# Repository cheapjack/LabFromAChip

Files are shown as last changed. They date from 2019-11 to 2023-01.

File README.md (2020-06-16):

# Lab-From-A-Chip

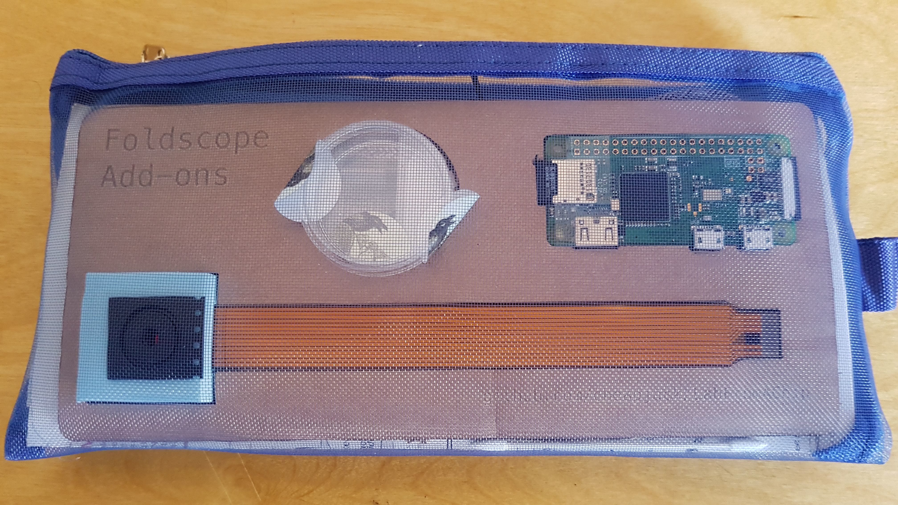
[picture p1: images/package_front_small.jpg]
Kit Component Net


Lab-from-a-chip is a DIY intervention in Lab On A Chip
technology using model organisms inspired by Science and Technology
studies and scientific practice and part of Ross Dalziel's PhD research, Critical Kits at the [Division for BioMedical Life Sciences at Lancaster University (BLS)](https://www.lancaster.ac.uk/biomedical-and-life-sciences/) and makerspace [DoESLiverpool](https://www.lancaster.ac.uk/biomedical-and-life-sciences).

*\"A* ***lab-on-a-chip*** *is a device that integrates one or several
laboratory functions on a single integrated circuit of only millimeters
to a few square centimeters to achieve automation and high-throughput
screening.\"* via
[Wikipedia](https://en.wikipedia.org/wiki/Lab-on-a-chip)

## Features

-   Hard silicon timer chips, the logical oscillating workhorses that
    make the world tick!
-   Stretchy see-through silicon polymers!
-   Lithium!
-   Model Organisms, Biology's non-human collaborators!
-   [Leeuwenhoek](https://en.wikipedia.org/wiki/Antonie_van_Leeuwenhoek)
    Microscopes made of paper with lenses ground in China on a tape reel
    just like electronic components!
-   The redundant media of Vinyl records!
-   Diodes!
-   Feminist technoscience!
-   Critters that move like animals but eat like plants!
-   Making moulds from the capitalist ruins!

## Included

 * [Foldscope](https://www.foldscope.com/) or 10x mag & up microscope
 * [PolyDiMethylSiloxane](https://en.wikipedia.org/wiki/Polydimethylsiloxane) (PDMS) Silicon
 * 2 Syringes
 * Mini Petri Dish
 * Glass or plastic Microscope slide
 * Glass coverslip
 * Instruction Booklet
 * Paperfuge Kit
 * Tweezers
 * Surplus electronics
 * 7"/12" vinyl record fragment

## Getting Started

Jump to [Getting Started](GettingStarted.md) to get going

## Background: Bridging The World-To-Chip Barrier

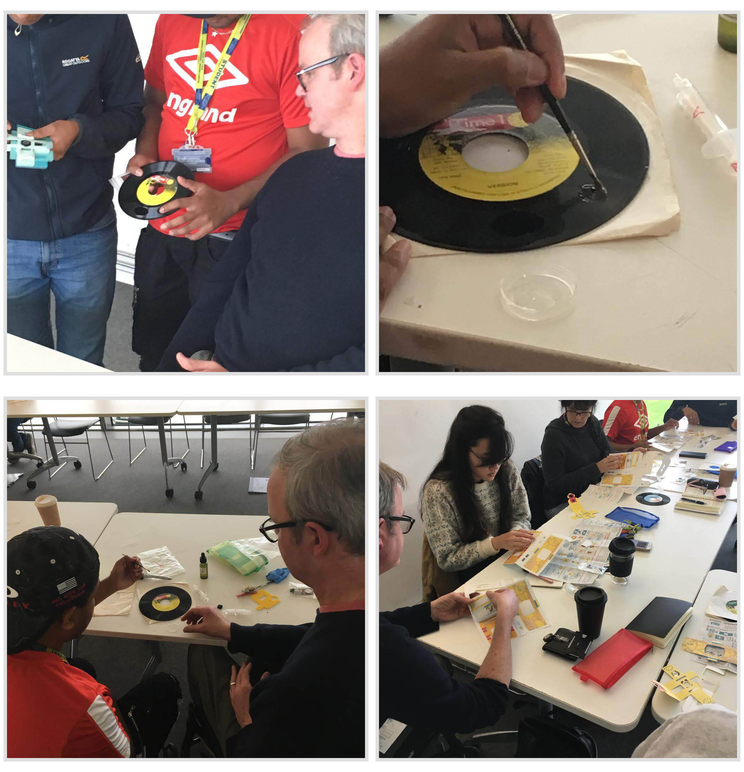
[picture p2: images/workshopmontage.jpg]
Workshop at Liverpool John Moores University with Dr Rod Dillon, 2019


This is part of Artist Ross Dalziel's art-science PhD embedded in the Division of Biomedical and Life Sciences at Lancaster University and makerspace [DoESLiverpool](https://doesliverpool.com), exploring critical making in kit cultures, *Critical Kits*. We're interested in what happens when you take a system from science and engineering, what Science and Technology Studies (STS) calls 'technoscience' and try to make it something that can be done outside of the "secluded research" (Callon et al. 2009. *Acting in an uncertain world : an essay on technical democracy* USA: MIT Press) of the science lab; how you could turn it into a DIY kit, what that entails and what that might mean.
  
We followed some diverse approaches to [DIY Microfluidics like this](http://fab.cba.mit.edu/classes/S62.12/people/tsai.liz/index.html), in our [Makerspace](https://github.com/DoESLiverpool/Wearables/wiki/Bio-Blog-2019#algae-microfluidics-doesliverpool) then began following the practices of microbiologist, researcher, biotechnologist and engineer [Alexandre Benedetto](https://www.lancaster.ac.uk/health-and-medicine/about-us/people/alexandre-benedetto).

Alex and his colleagues use the technique to observe the [organismal death process in *C elegans* model organisms](https://linkinghub.elsevier.com/retrieve/pii/S2211124718302316).Alex and his colleagues developed a method using the grooves of old vinyl records as moulds for PDMS silicon which centrifuged and de-gassed, provides optically clear environments for securing nematodes for the observation of gene expression and other processes.
 
We take ideas from STS and feminist technoscience to make a [Theoretical Repertoire](TheoreticalRepertoire.md) and develop a kit and workshop exploring model organisms in DIY environments made from discarded domestic electronics and media.

*"Microfluidic devices are an enabling technology for many labs,
facilitating a wide range of applications spanning high-throughput
encapsulation, molecular separations, and long-term cell culture. In
many cases, however, their utility is limited by a 'world-to-chip'
barrier that makes it difficult to serially interface samples with these
devices."*

(Longwell, Scott A, and Fordyce, Polly M. 2019. *micrIO: an open-source
autosampler and fraction collector for automated microfluidic
input--output* London Royal Society of Chemistry)

This world and it's related fields of engineering of pico, nano and microfluidics can be hard to get into. Engineering structures only a few tens of microns high are hard and expensive to make. Our project tries to take a playful approach to fostering agency and embodied thinking about this technology and bringing silicon and big living collaborating proteins (us humans) together.
 
We realised we are already surrounded by exotic objects that are made of very small engineered structures: the tiny logos etched onto integrated circuits in our phones or humble doorbell, or the tiny grooves of a vinyl record. All you need is some Polydimethylsiloxane (PDMS) a *silicon polymer* that is inert, non-toxic and optically clear to use these exotic objects to manipulate living organisms. What these chips really depend on is microfluidics, a development from electronic circuits but with things much bigger than electrons, the big molecules of chemistry and biology.
  
*"Microfluidic devices are powerful tools for biology, chemistry, and
medicine, with applications including biomolecular characterization,
cell encapsulation and culture, particle synthesis, and diagnostics. In
theory, their miniature scale allows a researcher to integrate processes
that span several lab benches into a single device with minimal cost and
sample requirements. In reality, the extensive infrastructure required
to convey reagents, samples, and analytes into and out of devices often
renders a 'lab-on-a-chip' more of a 'chip-in-a-lab"* (Ibid.)

Making this technology involves dust free environments, vacuum systems and expensive photolithography to get it done 'right'. But this usually does not stop the DIY 'maker' impulse. Even [Scanning Tunneling Microscopes (STM)](http://dberard.com/home-buit-stm) have gone DIY.  There is alot of open source work going on in the microfluidic community, not necessarily DIY, but I'm exploring how makerspaces can engage with it.

In experimenting with DIY microfluidics I hope to

-   Teach what microfluidics really are away from the master hyperbolic
    sales talk of Lab on A Chip.
-   Explore 'agency' and the power relations and subjectivities so other
    actors can explore the field
-   See what is going on in the technology

Make a *"frame for recovering the heterogeneous relations that technologies fold together...to be...re-enacted differently"* (Lucy Suchman, In Lury, C. and Wakeford, N. eds. (2012) Inventive methods: The happening of the social. London: Routledge. pp. 62-74.)

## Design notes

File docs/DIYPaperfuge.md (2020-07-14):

# DIY Paperfuge

Another Prakash Lab project, the makers of your Foldscope, is the Paperfuge, an "ultra-low cost, light-weight, field-portable centrifuge" based on the physics of a whirligig childrens toy. Our DIY version won't reach speeds of their design; but like our mould making, is 'just-good-enough' to let us follow a craft techniques in science. 

Recently some of their community used a [Dynamo torch](https://www.ebay.co.uk/itm/Pack-Hand-Pressing-3LED-Crank-Power-Dynamo-Wind-Up-Flashlight-Torch-Light-New/263717065208) using the mechanism to make the [Handyfuge](https://github.com/ethanjli/handyfuge). We're looking into remixing Bioengineer Ethan's design to fit our mini petri dishes as we'd get much faster spinning speeds. 

A centrifuge is a key tool in seperating the different parts of a solution like blood, cultured organisms or pond water. It's also a key part of preparing biological assays for [PCR](https://en.wikipedia.org/wiki/Polymerase_chain_reaction) or [LAMP](https://en.wikipedia.org/wiki/Loop-mediated_isothermal_amplification) diagnoses. 

Once you've mixed your PDMS carefully secure the lid (it's the bigger part) with the sellotape included, cut out the paperfuge design & push into the middle of the cut folds in your 'fuge & tape securely in position.

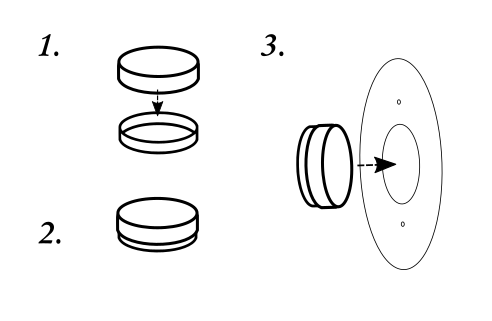
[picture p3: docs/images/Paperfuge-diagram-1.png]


## Cut out and make your Paperfuge 

Once you've mixed your PDMS, and before impressing our chip or vinyl fragment we will try to use the spin of the motion of a whirligig, the paperfuge. as a centrifugal force to 'push' the mix to the sides to make it nice & thin & even. 

Ideally we would assemble all our components in a dust & microbe free environment so we only see in the microscope what we might expect to see. For us, strange artefacts or particles from the unique histories of our moulds are encouraged!  

_Read the original Paperfuge research paper [here](http://dx.doi.org/10.1101/072207)_

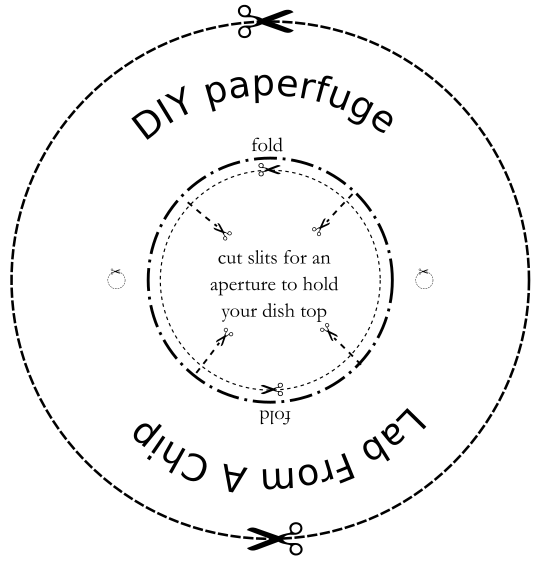
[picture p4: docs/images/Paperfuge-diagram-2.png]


Now thread the twine through the holes as below & tie off with a knot

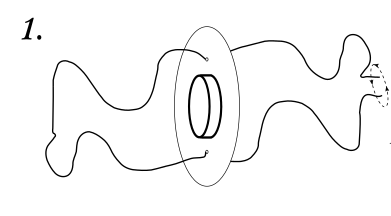
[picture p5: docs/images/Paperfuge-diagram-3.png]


Hold each end in front of you & start letting the disc rotate in front of you so that the twine starts to twist into a helix, it takes quite some time keep going! 
 
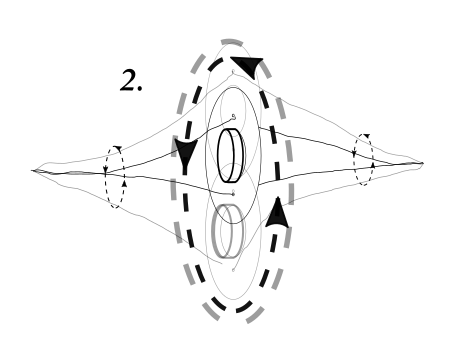
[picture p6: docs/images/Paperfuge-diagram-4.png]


Once twisted quickly pull the bunched up helix outwards to the side & watch it spin! The bigger the twist the faster your spin! Try it a few times before you make your vinyl or chip impression and set

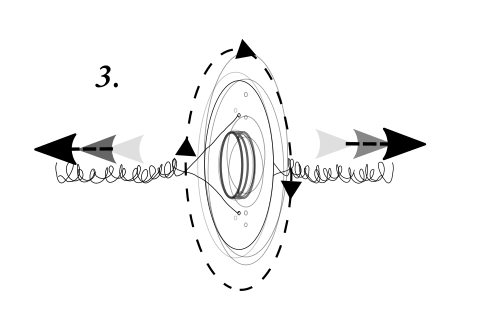
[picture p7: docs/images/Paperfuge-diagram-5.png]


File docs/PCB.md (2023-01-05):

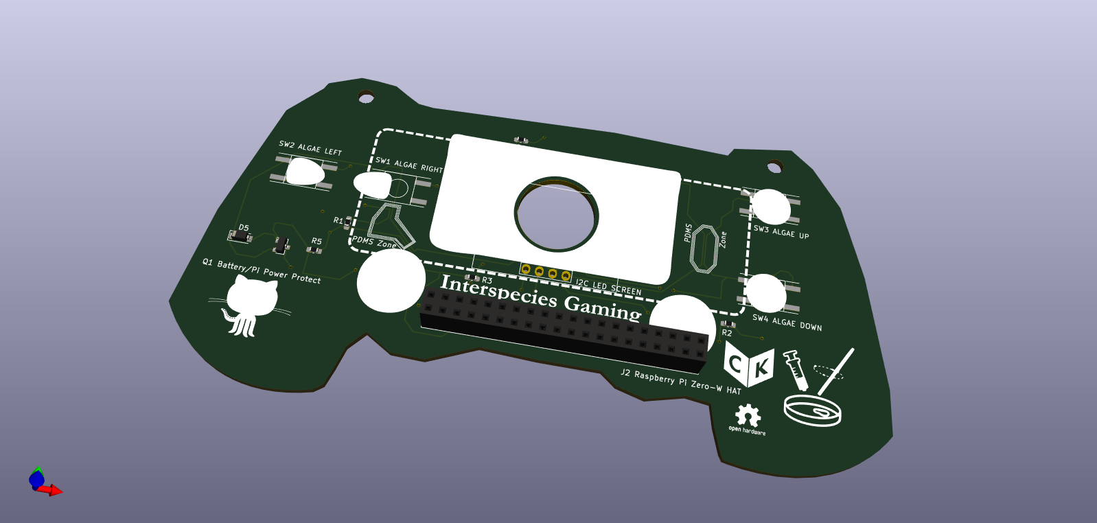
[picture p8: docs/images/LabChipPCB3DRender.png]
KiCAD render of the Lab From A Chip PCB Handheld Biotic Game Controller


## Lab From A Chip PCB 💾🔬🧪

The Lab From A Chip Printed Circuit Board (PCB) is a prototype game platform and Critical kit made using *Interleaving Practices*, a methodology developed by artist Ross Dalziel in his PhD research project at LICA (Lancaster Institute for Contemporary Arts) and the Division for BioMedical Life Sciences at Lancaster University (BLS) and makerspace DoESLiverpool. It is an 'add-on' kit for the *Foldscope*, a folding paper microscope by Prakash Labs.

Like the main Lab From A Chip project it's a material critique of bio-technology by way of an intervention in the field of what makers and researcher's like Riedel-Kruse et al. (2011) call 'biotic gaming' and Lamers and van Eck described in their review of key examples, 'Why Simulate? Hybrid Biological Digital Games' (2012), where 'live organisms are an integral part of digital gaming technology or player experience'. It followed from preliminary discussions of the idea of *Interspecies Gaming* with artist Isabel Paehr at the Disrupt Encode Consilidate international symposium organised by Dalziel and his colleagues and supervisors Neil Dawson and Rod Dillon at BLS in 2018. 

The PCB is not a novel art-science-tech object but rather the by-product of learning through careful critical making exploring how maker culture and microbiologists both exploit and care for each other through technology, in the case of makers and the non-human, in the case of biologists.

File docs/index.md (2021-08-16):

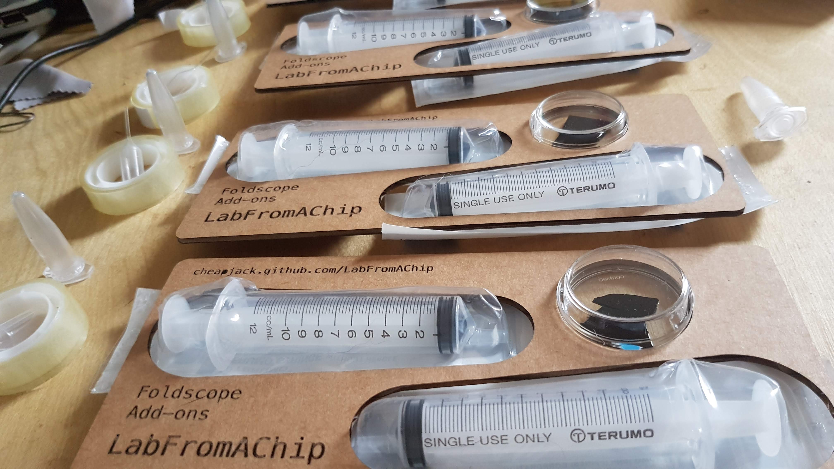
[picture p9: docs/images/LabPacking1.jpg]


Lab-from-a-chip is a DIY intervention in Lab On A Chip technology using model organisms inspired by Science and Technology studies and scientific practice and part of Ross Dalziel's PhD research, Critical Kits at the [Division for BioMedical Life Sciences at Lancaster University (BLS)](https://www.lancaster.ac.uk/biomedical-and-life-sciences/) and makerspace [DoESLiverpool](https://www.lancaster.ac.uk/biomedical-and-life-sciences).

*\"A* ***lab-on-a-chip*** *is a device that integrates one or several laboratory functions on a single integrated circuit of only millimeters to a few square centimeters to achieve automation and high-throughput screening.\"* via
[Wikipedia](https://en.wikipedia.org/wiki/Lab-on-a-chip)

We include a standard Foldscope kit fresh from the [Foldscope Shop](https://www.foldscope.com/) and have included some extra materials to help you get started in the world of DIY microfluidics. We include a sample test glass microscope slide ready to use with your foldscope which can be assembled from the pop out net of coloured paper components.

## Getting Started

Go to [Getting Started](./GettingStarted.md) to get making!

## Features

-   Hard silicon timer chips, the logical oscillating workhorses that
    make the world tick!
-   Stretchy see-through silicon polymers!
-   Model Organisms, Biology's non-human collaborators!
-   [Leeuwenhoek](https://en.wikipedia.org/wiki/Antonie_van_Leeuwenhoek) Microscopes made of paper with lenses ground in China on a tape reel just like electronic components!
-   The redundant media of Vinyl records!
-   Critters that move like animals but eat like plants!
-   Making moulds in the capitalist ruins!

## Included

Item|Number|Source
---|---|---
Foldscope|1|[Foldscope Shop](https://www.foldscope.com/)
[PolyDiMethylSiloxane](https://en.wikipedia.org/wiki/Polydimethylsiloxane)(PDMS) Silicon|1|[EBay Shop](https://www.ebay.co.uk/itm/0-5kg-Clear-Electronic-Potting-Compound-PV-Solar-Cell-Encapsulant-PDMS-RV/323393673289)
2 pouches with syringes `A` & `B`|2|[EBay Shop](https://www.ebay.co.uk/itm/Terumo-Sterile-Syringes-Hypodermic-Luer-Slip-Syringe-1ml-2-5ml-5ml-10ml-20ml-30m/263962579871)
35mm Mini Petri Dish|1|[EBay Shop](https://www.ebay.co.uk/itm/10-Pcs-Laboratory-Plastic-Petri-Dish-Sterile-Cell-Tissue-Culture-Dishes-35mm/292809086404)
Glass Microscope slide|1|[EBay Shop](https://www.ebay.co.uk/itm/Professional-50-pcs-Blank-Microscope-Slides-Cover-Glass-Lab-Prep-ground-edges/283412415605)
Pre-prepared glass microscope slide|1|DoESLiverpool community
Instruction Booklet|1|cheapjack
Tweezers|1|[EBay](https://www.ebay.co.uk/itm/10PC-TWEEZER-SET-FOR-PRECISE-ELECTRONICS-MODELLING-JEWELLERY-BEADING-WIRE-WORK/173541962441)
Surplus electronic chip|1|[EBay](https://www.ebay.co.uk/itm/NE555-Timer-Chips-5-Pack-IC-PCB-Free-UK-P-P/231668892136)
7"/12" vinyl record fragment|1|Found in a flat in the Holly Street Estate, Hackney 1996

<!--Glass coverslips|3|[Ebay Shop](https://www.ebay.co.uk/itm/100-Glass-Micro-Cover-Slips-Glass-Blank-Lab-Coverslip-Microscope-Slide-Cover/164281210287)-->

## Bridging The World-To-Chip Barrier

Workshop at Liverpool John Moores University with Dr Rod Dillon, 2019

This is part of Artist Ross Dalziel's art-science PhD embedded in the Division of Biomedical and Life Sciences at Lancaster University and makerspace [DoESLiverpool](https://doesliverpool.com), exploring critical making in kit cultures, *Critical Kits*. We're interested in what happens when you take a system from science and engineering, what Science and Technology Studies (STS) calls 'technoscience' and try to make it something that can be done outside of the "secluded research" (Callon et al. 2009. *Acting in an uncertain world : an essay on technical democracy* USA: MIT Press) of the science lab; how you could turn it into a DIY kit, what that entails and what that might mean.

We followed some diverse approaches to [DIY Microfluidics like this](http://fab.cba.mit.edu/classes/S62.12/people/tsai.liz/index.html), in our [Makerspace](https://github.com/DoESLiverpool/Wearables/wiki/Bio-Blog-2019#algae-microfluidics-doesliverpool) then began following the practices of microbiologist, researcher, biotechnologist and engineer [Alexandre Benedetto](https://www.lancaster.ac.uk/health-and-medicine/about-us/people/alexandre-benedetto).

Alex and his colleagues use the technique to observe the [organismal death process in *C elegans* model organisms](https://linkinghub.elsevier.com/retrieve/pii/S2211124718302316). Alex and his colleagues developed a mehtod using the grooves of old vinyl records as moulds for PDMS silicon which centrifuged and de-gassed, provides optically clear environments for securing nematodes for the observation of gene expression and other processes.

We take ideas from STS and feminist technoscience to make a [Theoretical Repertoire](./TheoreticalRepertoire.md) and develop a kit and workshop exploring model organisms in DIY environments made from discarded domestic electronics and media.

*"Microfluidic devices are an enabling technology for many labs,
facilitating a wide range of applications spanning high-throughput
encapsulation, molecular separations, and long-term cell culture. In
many cases, however, their utility is limited by a 'world-to-chip'
barrier that makes it difficult to serially interface samples with these
devices."*

(Longwell, Scott A, and Fordyce, Polly M. 2019. *micrIO: an open-source
autosampler and fraction collector for automated microfluidic
input--output* London Royal Society of Chemistry)

This world and it's related fields of engineering of pico, nano and microfluidics can be hard to get into. Engineering structures only a few tens of microns high are hard and expensive to make. Our project tries to take a playful approach to fostering agency and embodied thinking about this technology and bringing silicon and big living collaborating proteins (us humans) together.

We realised we are already surrounded by exotic objects that are made of very small engineered structures: the tiny logos etched onto integrated circuits in our phones or humble doorbell, or the tiny grooves of a vinyl record. All you need is some Polydimethylsiloxane (PDMS) a *silicon polymer* that is inert, non-toxic and optically clear to use these exotic objects to manipulate living organisms. What these chips really depend on is microfluidics, a development from electronic circuits but with things much bigger than electrons, the big molecules of chemistry and biology.

*"Microfluidic devices are powerful tools for biology, chemistry, and
medicine, with applications including biomolecular characterization,
cell encapsulation and culture, particle synthesis, and diagnostics. In
theory, their miniature scale allows a researcher to integrate processes
that span several lab benches into a single device with minimal cost and
sample requirements. In reality, the extensive infrastructure required
to convey reagents, samples, and analytes into and out of devices often
renders a 'lab-on-a-chip' more of a 'chip-in-a-lab"* (Ibid.)

Making this technology involves dust free environments, vacuum systems and expensive photolithography to get it done 'right'. But this usually does not stop the DIY 'maker' impulse. Even [Scanning Tunneling Microscopes (STM)](http://dberard.com/home-buit-stm) have gone DIY.  There is alot of open source work going on in the microfluidic community, not necessarily DIY, but I'm exploring how makerspaces can engage with it.

In experimenting with DIY microfluidics I hope to

-   Teach what microfluidics really are away from the master hyperbolic
    sales talk of Lab on A Chip.
-   Explore 'agency' and the power relations and subjectivities so other
    actors can explore the field
-   See what is going on in the technology

Make a *"frame for recovering the heterogeneous relations that technologies fold together...to be...re-enacted differently"* (Lucy Suchman, In Lury, C. and Wakeford, N. eds. (2012) Inventive methods: The happening of the social. London: Routledge. pp. 62-74.)

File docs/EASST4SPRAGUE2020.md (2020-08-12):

#  Lab From A Chip
Programme of Making and Doing Session at [EASST4SPRAGUE2020](https://www.easst4s2020prague.org/)

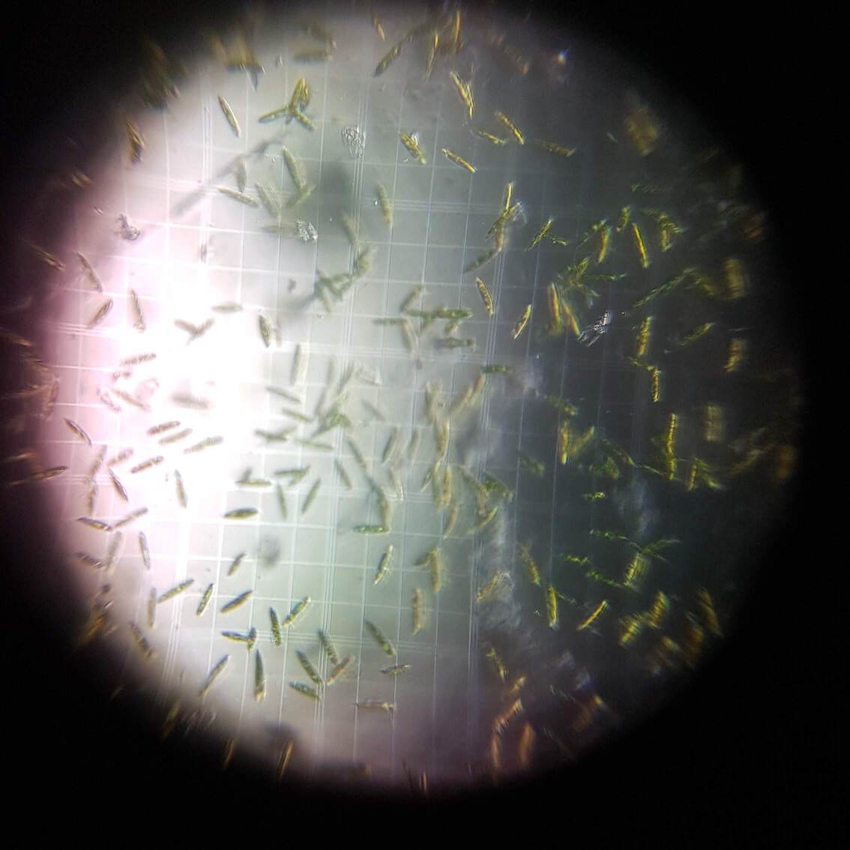
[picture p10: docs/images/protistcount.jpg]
*Euglena gracilis* on a hemocytometer viewed under a DIY lasercut microscope


## Getting Started

Already received your kit? Head over to the [Getting Started Guide](GettingStarted.md)

## Abstract

We ask questions as we build little logical maps together with *Euglena gracilis*; why are diodes so cheap, how do worms die? What organisms should we play with and how do old 7-inch vinyl records, Printed Circuit Boards (PCB's), Integrated circuits (IC's) A.K.A. silicon chips and other surplus domestic artefacts provide physical spaces to tell stories and learn critical knowledge? We explore this through 'kit culture', hands-on by using a prototype 'educational' kit and the emerging method of 'Interleaving Practices', part of artist-researcher Ross Dalziel's art-science practice and PhD research embedded in Lancaster University.

## Brief Description

Remote hands on making & doing session, featuring paper folding microscopy and micro-fluidics, so called 'lab-on-a-chip' technology. Materials will be provided as a kit posted to `EASST4SPRAGUE2020` participants who sign up to the activity prior to the online conference. Participants in their homes or safe spaces, will be led remotely by the artist-presenter-researcher on a screen sharing video platform in a making and doing session with these kits at `EASST4SPRAGUE2020`.

 Our new worlds of locating and timing is an opportunity to warp the time of the activity we normally get to engage with each other at our EASST meetings; the 'educational kit' format the session uses allows us to do this; some of the activity needs 1 or 2 days preparation and experiment prior to the activity, so the session will require some commitment to playing with materials to get the most out of it.

 We'd like to focus on all of our experiences with the kit so we see this as an experimental and informal show and tell more than a presentation online. Numbers are limited to available kits so we have a core group of engaged people.

We'll provide more information to participants who sign up with respect to online presentation dates and timings soon. We'll also include further information on the PhD research behind the session with an opportunity to engage further and health and safety information with respect to the packing and preparation of the kits.

We also welcome ongoing engagement and hope we can start some kind of collective and engage further with all of our research practices.

The project homepage provides updated further information and guidance

[cheapjack.github.io/LabFromAChip/](https://cheapjack.github.io/LabFromAChip/)

## Methods

It's a playful DIY approach to kit making, a key feature of Ross' work and his collaborators at [Domestic Science](https://domesticscience.org.uk/) and [DoESLiverpool](https://doesliverpool.com/). These kits are emerging, messy and unfinished; they 'bag up' & include existing kits, primarily the [Foldscope](https://www.foldscope.com/) and are at once a kind of literature review, fan-non-fiction and remix; your interactions will inform their future story. Once you receive your kit you will be able to use model organisms and surplus integrated circuits (IC's) included, the black boxes of microbiology and computer science. We'll learn how to make DIY micro-fluidic moulds, following the practices observed in Ross' research developed by researchers and teaching staff in the Division of Biomedical and Life Sciences (BLS) at Lancaster University.

For us science studies is a theoretical repertoire for a form of 'critical making', implosions & configuration methods (Ratto, Haraway, Dumit, Suchman) developed in an art practice embedded in microbiological pedagogy, the teaching space of BLS Lancaster and makerspace culture. The repertoire helps us 'unbox' an "infinity of traces" where the convenient mobilities of PCBs, biotech and interspecies gaming become not-so-humble-bundles of love, education, mobility, identity and inequality.

This helps inform, 'Interleaving practices' the artist-researchers emerging method for working with people in the diverse disciplines and domains of biomedical technoscience using the format of what we think of as 'kit culture', a mix of so-called STEAM education and makerspace culture. From here we negotiate the "World to chip barrier" (Longwell, Scott A, and Fordyce, Polly M. 2019. *micrIO: an open-source autosampler and fraction collector for automated microfluidic input–output London Royal Society of Chemistry*) where the 'revolutionary' promise of 'Lab-On-A-Chip' technology often becomes "A-Chip-In-A-Lab" (Ibid.). Kits here are boundary objects to support ongoing, troubling and messy explorations of biopolitics and cross species value extraction and a chance to see how much of this can be carried along in a kit format.

Participants having received their kits will use included [Foldscopes](https://www.foldscope.com/) with their smartphones and other included DIY lab materials to make non-toxic Polydimethylsiloxane (PDMS) silicon moulds from surplus 555 timer chips and the grooves of a fragment of a 7 inch vinyl record from a long gone Lovers Rock record label. Together, online and in our hands, we will try to play with, yet fail to care-for-fully, Euglena gracilis a heterotrophic protist algae, as hungry and motile as an animal, yet as resilient as a photosynthesising plant.

## Relevance

The silicon chip is a substrate for knowledge and mobility, enabling both washing machines and big DNA data, Gutenberg style embodiments of knowledge and punitive discipline, shaped by specific historical material arrangements. Data colonialism, public imaginaries and commons work upon it and through it. The who, how, why and where of making and maintaining them, matters. They are a political cut in the world, a revolutionary space, yet the masters tools for the master's house. We follow the hyperbole and reality of Lab On A Chip bio-tech to try to develop hybrid forums to re-configure these devices, the geographies they make and the crises they work in.

Ultimately we explore how much of this can be carried along in a cheap easy to distribute kit of materials and what ways of knowing it can be part of.

## Thematic Clusters

Experiments in Collaboration and Critical Participation
Multispecies Assemblages, Life Sciences, Queer Ecologies

## Other Thematic Cluster

Material activism, Kit making culture

## Technical Information

Online video platform information will be provided.
[Included](https://cheapjack.github.io/LabFromAChip/#included)

## Project URL

[cheapjack.github.com/LabFromAChip](https://cheapjack.github.com/LabFromAChip)

## Author
(Presenter-Artist-Researcher)
<a href="mailto:r.dalziel@lancaster.ac.uk?subject=Lab From A Chip at EASST4SPRAGUE2020">Ross Dalziel</a> 

## Getting Started

Already have your kit? checkout the [Getting Started guide](https://cheapjack.github.io/LabFromAChip/GettingStarted)

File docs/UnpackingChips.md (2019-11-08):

## Wednesday 13th November 2019

### STS Work in Progress



## What STS methods am I actually using?

Case Study
Configurations?
ethnography,
actor network theory,
Social practice theory,
art interventions,
digital methods

## Theoretical Repertoires

The impact of my literature review is the enriching of theoretical repertoires, which means all of the above can be unpacked. I pay attention differently now.

## What is unpacked from my PDMS chip impression?

* Just using mass produced waste or an existing manufactured item like this rather than building a fresh expensive photo-lithographic microfluidic plate, using 'cheap' domestic sources, similar to Alex's students using vinyl records, means discussions can be had about everything from supply chains, to the 'social' cost of mass manufacturing and it's histories of imperialist labor extraction
* This coincides with the of tracking supply chains and energy toxicity; Adrian and I have suggested adding fields to the BOM `.tsv` files to include where it was made, by whom and some sort of energy/carbon useage.
* So for my wearable sensor badge we'll be calculating and including this information as part of the tutorial and documentation of the kit. We want to normalise the practice of including bodily material histories.
* **Coomassie Blues**: an idea Rod & I had about exposing the supply chains and histories of the day to day materials used in microbiology lab practices
* ***Staying with the trouble*** by using things `already-dug-out-of-the-ground`
* Callback: The Biol387 students use Wilkos as their source for studying the genetic geneaology of yeast
* They help me when I need to explain critical kits to science students and scientists
* Using an ESP32 integrated circuit attracts makers interested in IoT; it's the arduino of IoT. It can start conversations about scale & micromilling in electronics production; and then alongside:
   * Why the algae? why the annoying externalities excluded from manufacturing?
   * A good chip needs to be isolated from the world and you need to make a million of them before young people can access them... etc
   * How do we protect rivers from the market imperative to make LEDs for £0.001?
     * Adrian McEwen and
* It's part of a series of FoldScope 'add-ons' that I've been making inspired by Lucy Suchman's *'artful integrations'*
  * Pi Zero Camera Twitch streaming Add-on based on [Makespace Live](https://github.com/DynamicDevices/makespacelive)
  * A wearable add on to help steady foldscopes in the field for wheelchair users
  * Microfluidic stickers to capture microfluidic environments
* Deciding to place my work in the 'domestic' or on a golf course, or in a makerspace; **i.e.** definitively in the social and not some independent ontology of art is a specific decision. It's a political 'cut'. My enriched repertoire has made me see what cuts I am making.    

### Lab-from-a-chip

Unboxing the PDMS Death Disco: A Case Study of FoldScope by making add-on Kits

[Critical Kit PDMS tweet with video of algae](https://twitter.com/CriticalKits/status/1171435079953833985)

I have been making microfluidic environments by making impressions of discarded electronics in the makerspace, based on Alex Benedetto and I talking about doing this in domestic environments; like kitchen cloths electronics, utensils or textiles.

This is partly a review of the FoldScope which Im using as a case study in my literature review.

It has all the intersections of biology, engineering, well meaning utility and agency for frugal science in 'intractable' places

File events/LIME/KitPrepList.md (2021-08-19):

## Kit Prep

## Shopping List

Item|Number|Source|In Stock|Ordered|Notes|Cost
---|---|---|---|---|---|---
Foldscope|1|[Foldscope Shop](https://www.foldscope.com/)|<input type="checkbox" checked>|<input type="checkbox" unchecked>||£0
Disposable hand pipette|20|[EBay](#)|<input type="checkbox" unchecked>|<input type="checkbox" unchecked>||£3
1.5ml Eppendorf Tube with click lid|20|[EBay](#)|<input type="checkbox" unchecked>|<input type="checkbox" unchecked>||£3
[PolyDiMethylSiloxane](https://en.wikipedia.org/wiki/Polydimethylsiloxane)(PDMS) Silicon|1|[EBay Shop](https://www.ebay.co.uk/itm/0-5kg-Clear-Electronic-Potting-Compound-PV-Solar-Cell-Encapsulant-PDMS-RV/323393673289)|<input type="checkbox" checked>|<input type="checkbox" unchecked>||£18.50
2 pouches with syringes `A` & `B`|20|[EBay Shop](https://www.ebay.co.uk/itm/Terumo-Sterile-Syringes-Hypodermic-Luer-Slip-Syringe-1ml-2-5ml-5ml-10ml-20ml-30m/263962579871)|<input type="checkbox" unchecked>|<input type="checkbox" unchecked>||£7.99
Sticker Set|20|Sticker Company|<input type="checkbox" unchecked>|<input type="checkbox" unchecked>||£10
35mm Mini Petri Dish|20|[EBay Shop](https://www.ebay.co.uk/itm/223684097317)|<input type="checkbox" unchecked>|<input type="checkbox" unchecked>||£5.62
Glass Microscope slide|20|[EBay Shop](https://www.ebay.co.uk/itm/203458550468)|<input type="checkbox" unchecked>|<input type="checkbox" unchecked>||£4.50
Pre-prepared glass microscope slide|20|DoESLiverpool community|<input type="checkbox" checked>|<input type="checkbox" unchecked>||£0
Instruction Booklet|20|cheapjack|<input type="checkbox" unchecked>|<input type="checkbox" unchecked>||£35
Tweezers|1|[EBay](https://www.ebay.co.uk/itm/10PC-TWEEZER-SET-FOR-PRECISE-ELECTRONICS-MODELLING-JEWELLERY-BEADING-WIRE-WORK/173541962441)|<input type="checkbox" unchecked>|<input type="checkbox" unchecked>||£13.77
Surplus electronic chip|20|[EBay](https://www.ebay.co.uk/itm/NE555-Timer-Chips-5-Pack-IC-PCB-Free-UK-P-P/231668892136)|<input type="checkbox" unchecked>|<input type="checkbox" unchecked>||£12.30
7"/12" vinyl record fragment|20|Found in a flat in the Holly Street Estate, Hackney 1996|<input type="checkbox" checked>|<input type="checkbox" unchecked>||£0
*LIME TOTAL*||||||**£54.18**

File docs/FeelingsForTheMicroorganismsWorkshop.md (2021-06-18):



Lab-from-a-chip is a kit for collaborating with microscopic model organisms - freshwater algae - inspired by the practices of microbiology, maker culture and Science and Technology studies, part of artist Ross Dalziel's PhD research - a form of art-science - at the [Division for BioMedical Life Sciences at Lancaster University (BLS)](https://www.lancaster.ac.uk/biomedical-and-life-sciences/) and makerspace [DoESLiverpool](https://www.lancaster.ac.uk/biomedical-and-life-sciences).

With collaborators at [Domestic Science](https://domesticscience.org.uk/) our workshop uses safe simple accessible micro moulding techniques to interact with the microscopic material surfaces of our everyday modern world - the surfaces of a microchip, an old vinyl record, the texture of a phone case - with living photosynthetic algae.  

We use a standard Foldscope kit fresh from engineer Manu Prakash's [Foldscope Shop](https://www.foldscope.com/) with extra materials to help people explore the world of DIY microfluidics.

## Feeling For the Microorganims

We are inspired by Evelyn Fox Keller's fascinating biography of geneticist Barbara McClintock, *A Feeling For The Organism* and the intimate care for living things - human and non-human - required of all workers in the life sciences. This workshop aims to explore and reflect on the value of everyday biomedical research and practice - a 21st century domestic science that considers everyone's labour - particularly in biomedicine, health and wellbeing - and aims to reconnect to our passions to look after organisms other than ourselves. 

## Features

 * Play with silicon chips and the surfaces of the technoscientific materials we use everyday.  
 * Pay with stretchy see-through hands on food safe silicon polymers!
 * Model Organisms, Biology's non-human collaborators!
 * [Leeuwenhoek](https://en.wikipedia.org/wiki/Antonie_van_Leeuwenhoek) style DIY orgigami Microscopes by [Foldscope](https://www.foldscope.com/)
 * *Euglena gracilis* algae, critters that move like animals but eat like plants
 * Making microscopic moulds from everyday technology and capturing images with smartphones, computers and the naked eye

## Background

Workshop at Liverpool John Moores University with Dr Rod Dillon, 2019

This is part of Artist Ross Dalziel's art-science PhD embedded in the Division of Biomedical and Life Sciences at Lancaster University and makerspace [DoESLiverpool](https://doesliverpool.com), exploring critical making in kit cultures, *Critical Kits*. We're interested in what happens when you take a system from science and engineering, what Science and Technology Studies (STS) calls 'technoscience' and try to make it something that can be done outside of the "secluded research" (Callon et al. 2009. *Acting in an uncertain world : an essay on technical democracy* USA: MIT Press) of the science lab; how you could use this to reflect on healthy relationships, care and maintenance of the world .

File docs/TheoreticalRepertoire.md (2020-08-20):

## Theoretical Repertoire 📚 📦

See [our theory presentation here](https://fuzzy-scabiosa.glitch.me/)

In my research on kit culture, I try to build up a theoretical
repertoire for tuning into what might be going on across various forms
of biological knowledge production, then use this repertoire to make
kits, a kind of `critical-making`.

These kits then become handy "boundary objects", objects that people
from different disciplines or practices can use or understand, for
exploring further and more intimately, growing the repertoire, making
more kits with more people and so on. In my case they allow an artist
doing research, 'laypersons'(different 'publics') and
'specialists'(scientists and their students) understand each other.

But also and this is what I now understand as a big part of my artistic
practice and the practice of [Domestic
Science](https://domesticscience.org.uk/about.html), most commonly the
kits and activities I make and facilitate become objects to talk over
and around.

I build the repertoire by reading through making, making through reading
and talking.

-   Review a range of kit and kit like practices that condense into a
    [Library of
    kits](https://domesticscience.org.uk/criticalkits/Library.html), a
    kit literature.
-   Briefly review literatures of the history of the philosophy of
    science in response to practices and kits I make with people.
-   Review literatures in STS Method, structured by emerging kits.

With this repertoire and armed with my boundary negotiating kits:

-   Observe Craft practices in teaching microbiology undergraduates at
    the Division for Biomedical Life Science at Lancaster University
-   Observe me making kits with researchers and students
-   Making kits and facilitating activity based on them in makerspace
    DoESLiverpool and other sites in the worlds related to my art
    practice.

### Imaginaries

STS method includes the use of ethnographic or other styles of 'case
study'. This kit is one such emerging case. Ideas like socio technical
imaginaries are relevant when thinking about what is really going on in
powerful ideas like ***Lab on a chip***

*"Throughout the modern world, science and technology (S&T) are deeply
implicated in producing collective visions of good and attainable
futures. These "sociotechnical imaginaries" have proved particularly
useful for policymakers in late modern societies. Imagined futures help
justify new investments in S&T; in turn, advances in S&T reaffirm the
state's capacity to act as responsible stewards of the public good.
Sociotechnical imaginaries serve in this respect both as the ends of
policy and as instruments of legitimation.*

*...but other imaginaries are also often at play in the world, based on
different cultural understandings of the good life. Public hopes and
fears concerning S&T engage in unpredictable ways with forms of
imagination current in policy worlds. Publics also construct and act
upon their own imaginaries of those in power and hold policymakers
responsible in accordance with their tacit or explicit notions of
discovery, innovation, efficiency, progress, uncertainty, evidence,
argument, value, legitimation.*

*Another way to understand a concept is to see how it works alongside
others....imaginaries help explain why, out of the universe of
possibilities, some envisionings of scientific and social order tend to
win support over others---in other words, why some orderings are
co-produced at the expense of others.\"*

From [The Sociotechnical Imaginaries
Project](http://sts.hks.harvard.edu/research/platforms/imaginaries/)

### The Lab-On-A-Chip Imaginary

Lab on a chip tech builds an interesting 'public imaginary', a narrative
for both layperson and specialist, as a form of biological or chemical
manufacturing akin to the so called silicon 'revolution'.

Like Integrated circuits they are very small environments for
manipulating and interpreting the behaviour of matter. Like their
silicon cousins they generate alot of hype, hope, fear, hard cash and
financialisation and hopefully something 'good'.

Unlike these circuits, lab-on-a-chips manipulate much bigger things than
electrons, big, scary molecules just as weird as any tiny quantum
packets, but so complicated it can make your head spin as fast as an
accountant at the Large Hadron Collider: big proteins like DNA,
bioassays and super collaborating symbiotic mega-communities which have
the added complication of not only ***being alive*** but containing mind
boggling histories encoded inside every part of them.

What **Lab on a chip** imaginaries are made?

-   Scalable distributable labs that work 'on their own'
-   Disrupting the field of bio and chemical manufacturing
-   Somehow it's intelligent, and automated
-   Labs can work 'anywhere'
-   Labs are small but powerful
-   Myths of new biological computers made by existing biological
    computers
-   These are like kits: they package up some bio processes and make
    them super mobile and easy
-   They are going to 'revolutionise' access to the industry, which you
    can see in the [Metafluidics](https://metafluidics.org/)\
-   Realise the genetics-to-order shop scenes of science fiction like
    Bladerunner etc.\
-   It has all the intersections of biology, engineering, well meaning
    utility and agency for frugal science in 'intractable' places

### Invisible Work

*"I took exception to a comment on maker education twitter a while back
that kits used in tech education workshops are a great idea because they
'save time' in workshops; this could not be further from the truth. That
well meaning comment unintentionally reveals what's missing in
understanding kits and by extension the whole maker meme and from there,
other creative practice that uses technology in social settings: The
care, thought, iterative failure, maintenance and communal resilience
required for their success."*

[My blog on Critical
Kits](http://cheapjack.github.io/2018/07/05/critical-kit-resilience)

This chimes with Susan Leigh Stars description of the invisible work
that goes on behind scientific facts and products

*"People may see a map of a genome or a syringe full of experimental
medication. These are just the end products, however, of a web of
relationships, what Lave and Wenger have called communities of practice.
Lave and Wenger make the strong claim that membership in these
communities constitutes learning and science (Adler and Obstfeld, in
press; Bowker and Star, 1999: Chapter 10; Lave and Wenger, 1991;
Obstfeld, 2005). These relationships are usually invisible to readers of
science and technology (Star and Strauss, 1999; Suchman, 1987)."*

(Bryant, Anthony. Charmaz, Kathy ed. (2011) *The SAGE handbook of
grounded theory* Los Angeles: Sage

*"Scientific journals are full of articles that delete the development,
setting, communication practices, and 'grunt work' involved in doing
science."*

(Ibid.)

#### Configuration

***Configuration*** takes these imaginaries further and feel
particularly relevant to the 'invisible work' and 'talking' that are
bound up in science, technology and kit making

*"drawing our analytic attention to the ways in which technologies
materialize cultural imaginaries, just as imaginaries narrate the
significance of technical artefacts."*

*\"\"Configuration, I have suggested here, is part of a toolkit for
thinking about constitutive and generative, reiterative and
(potentially) transformative material-semiotic conjoining. In the case
of technology, configuration orients us to the entanglement of
imaginaries and artefacts that comprise technological projects.*

*While normative methods are designed to define and police boundaries,
configuration as a method assemblage aims to articulate method in a way
that opens received and/or congealed relations to being re-enacted
differently (see Law, 2004: 84).\"*

(Suchman, Lucy. *In Lury, C. and Wakeford, N. eds. (2012) Inventive
methods: The happening of the social.* London: Routledge. pp. 62-74.)

Inspiring Interventions
-----------------------

[Mikroskopisk PacMan](https://youtu.be/GvZm9EXqrdU) Erik Andrew
Johannessen's high end microfluidics game is worth looking at for a
playful exploration. Check out the [full video
here](https://www.youtube.com/TVxNvWCTbYo) and read the [Vice
article](https://www.vice.com/en_us/article/vv7zba/pac-man-inspires-norwegian-researchers-to-better-study-microorganisms)
if you like that kind of thing. Back in the 1960s when the military
funded the shrinking of transistors nobody thought they'd use it for fun
with ghosts, stories and pictures of cats, just bombs and tracking
communists, but just look at the weird cultures that turned into! I
wonder where microfluidics will take us? Should we be even doing this?
What knowledge and 'goods' does it make?

Helen Pritchard's [Critters on a
chip](http://www.helenpritchard.info/artworks-projects/critter-compiler-prototype-2016)
suggests we might get organisms in microfluidic environments writing
code and literature.

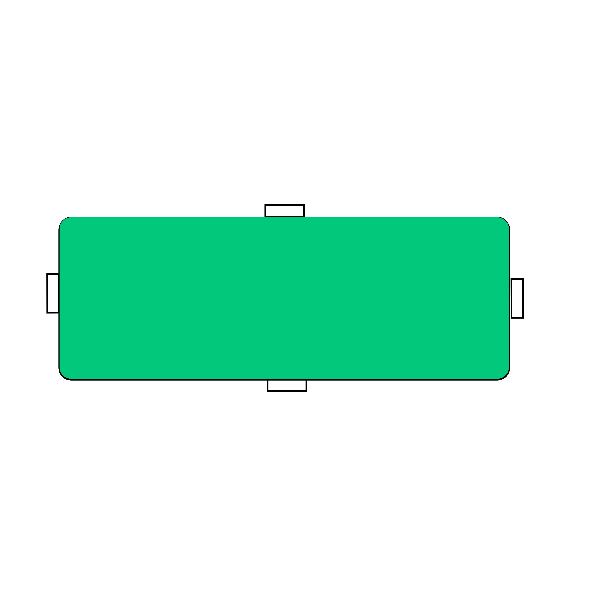
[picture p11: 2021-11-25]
LabChipPCB/.svg2shenzhen-cache/images/F.Silk_g8169.png

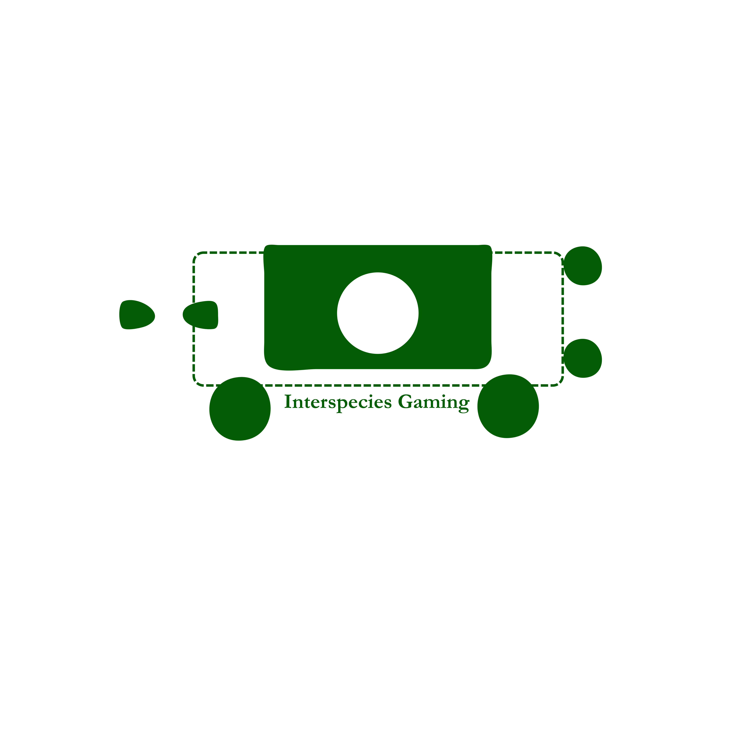
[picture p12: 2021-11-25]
LabChipPCB/LabChipPCB/.svg2shenzhen-cache/images/F.SilkS_g2002.png

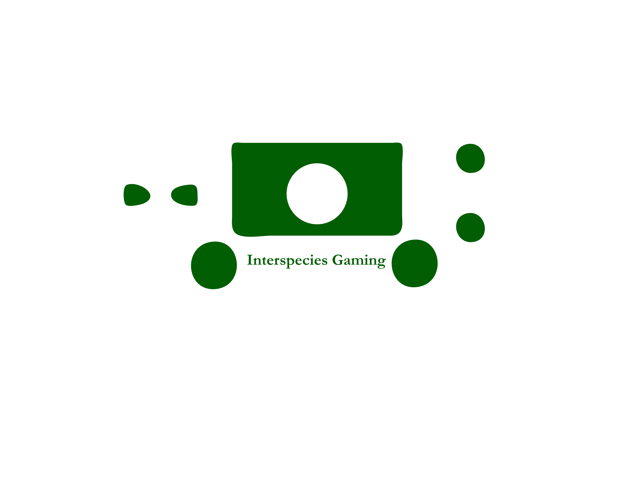
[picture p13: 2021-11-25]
LabChipPCB/LabChipPCB/.svg2shenzhen-cache/images/F.SilkS_g8012.png

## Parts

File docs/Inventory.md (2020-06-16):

### Inventory 

Item|Number|Source
---|---|---
Foldscope|1|[Foldscope Shop](https://www.foldscope.com/)
[PolyDiMethylSiloxane](https://en.wikipedia.org/wiki/Polydimethylsiloxane)(PDMS) Silicon in 2 syringes `A` & `B`|1|[EBay](https://en.wikipedia.org/wiki/Polydimethylsiloxane)
`A` & `B` Syringes|1|Shop
Mini Petri Dish|1|Shop
Glass Microscope slide|1|EBay
Glass coverslip|1|Ebay
Pre-prepared glass microscope slide|1|DoESLiverpool community
Instruction Booklet|1|cheapjack
Paperfuge Kit|1|cheapjack
Twine|1|cheapjack
Tweezers|1|EBay
Surplus electronic chip|1|DoESLiverpool
7"/12" vinyl record fragment|1|A flat in the Holly Street Estate, Hackney 1996

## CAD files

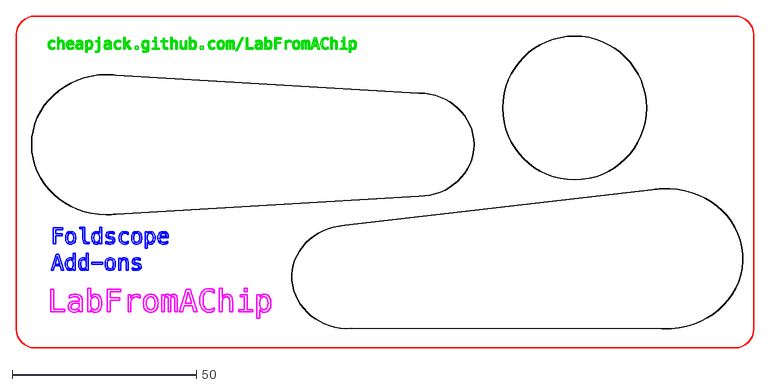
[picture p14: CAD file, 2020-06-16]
builds/FoldscopeAddOn1.dxf
199.9 x 90.0

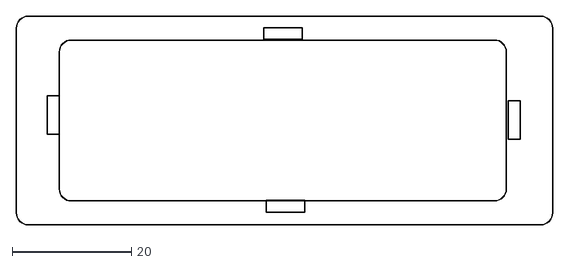
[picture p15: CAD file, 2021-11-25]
LabChipPCB/PCBShapeWithSlide.dxf
90.0 x 35.0

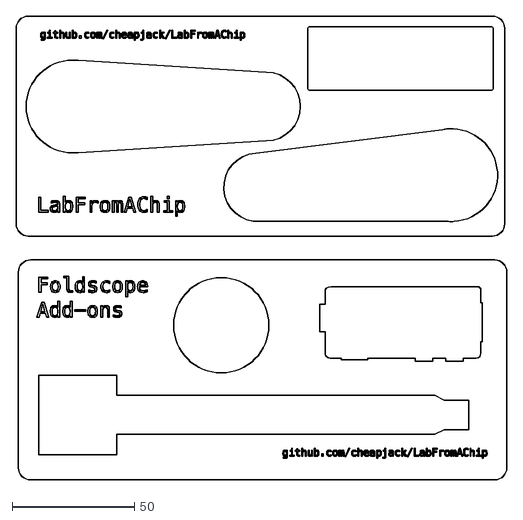
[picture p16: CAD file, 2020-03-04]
builds/FoldscopeAddOnPiZero.dxf
200.9 x 189.8

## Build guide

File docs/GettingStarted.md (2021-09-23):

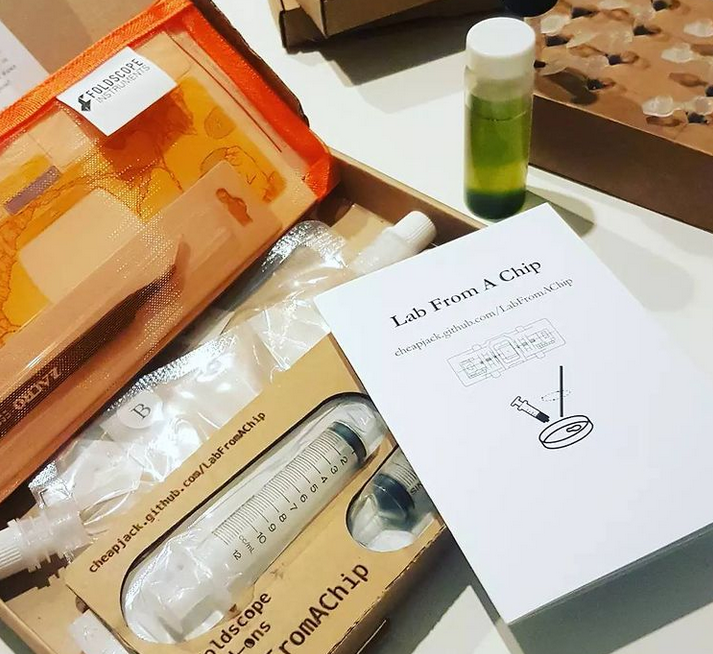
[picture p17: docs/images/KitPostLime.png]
Kits ready for postage


## Welcome To A Feeling for the (Micro) Organisms! ⚠ ️

Now you've received your kit please open when you receive it and leave it in sunlight so the testtube taped to the lid of your kit box is exposed to sunlight - this contains your supply of cultured algae and they need sunlight to stay alive! You also need to carefully open the lid and 'snap' close it again to allow gases to exchange every few days to ensure they stay healthy and thriving between workshops and hopefully keep the colony going for as long as possible - which will be a nice rewarding goal to aim for I think.

## First Session🔬📲

We'll be going over microscope use in our first session and then doing the moulding element together in session so please leave the moulding till later. In the clip I mention that there will be a moulding video but I think it will be better to do this 'together' online. The instruction booklet is then there for future reference. So play with your assembled 'scope if you can, but dont worry if you don't have time or are unable to do it for any reason (you don't need to give a reason!). You can still take part and assemble the scope in the first session or whenever you want.

So just to be clear, if you are taking part in the online workshops, don't start the moulding process, just familiarize yourself with the kit and process and play with the included paper slides, we'll do the moulding together!

***Click on the YouTube Clips below for introductions to your Foldscope and LabFromAChip kit!***

### Assembly

<iframe width="560" height="315" src="https://www.youtube.com/embed/HHnZEMIfX6k" title="YouTube video player" frameborder="0" allow="accelerometer; autoplay; clipboard-write; encrypted-media; gyroscope; picture-in-picture" allowfullscreen></iframe>

### PDMS Moulding Guide

Coming soon!

### Set mould Slide Preperation & Phone viewing

<iframe width="560" height="315" src="https://www.youtube.com/embed/sF9TxsjTpCg" title="YouTube video player" frameborder="0" allow="accelerometer; autoplay; clipboard-write; encrypted-media; gyroscope; picture-in-picture" allowfullscreen></iframe>

## Overview

You now have a genuine foldscope classroom kit with some extras to help you experiment in DIY microfluidics with the PDMS silicon provided in the pouches labelled `A` & `B`

These extras include the Lab From A Chip instruction booklet to help with the microfluidic elements of the kit for viewing the included live algae samples. Once you receive your kit open it up and make sure your algae sample gets lots of light to help keep them alive!

## Preperation: Foldscope Assembly & Testing ⚙️

The first thing to do is to assemble and get used to using your Foldscope. This takes some practice to get everything assembled and be comfortable viewing something.

Fully fold out the included colour cardboard net; this contains all the foldscope components that you 'pop' out of the net and fold together with the magnetic lens couplers and lenses in the bubble wrap envelope. Unfold the instruction booklet and read both sides and follow the instructions to make your foldscope.

There is an [online user guide](https://www.foldscope.com/user-guide) and [series of tutorials](https://www.foldscope.com/tutorials) on the official Foldscope website and their YouTube channel especially is super helpful.

It takes time to get consistent images with your phone which is what we are aiming for so you can share your images and keep a record of your experiments. You need to practice. Once you get used to it you can make a really simple 'Quickstart Minimal Build described below if you're swapping between lots of different slides.

### Reference Glass Slide

We've included a ready made glass microscope slide in the plastic bag inside the foldscope kit. Use this to 'test' your foldscope build and focussing skills so make sure once assembled you [watch the glass slide tutorial](https://www.youtube.com/watch?v=z4qLuXhI3pI) to help you test the microscope. The slides are labelled and the sample is randomly chosen from an amateur biologist's collection, typical of the slides you might find in a beginners or children's microscope kit, but ready to view and some of them even stained to help you see the structures. If you can resolve a clear image of this slide and take a picture on your smartphone camera then you are ready to start making your own slides with PDMS moulds.

You'll find you need some effort to insert the slide into the frame - but the elasticity of the coated paper of the 'scope can stretch to accommodate - it's good to loosen it in this way so that when you insert your custom slide you won't damage your sample or PDMS slab

We've also included a reuseable glass slide for your PDMS work - again inside the clear plastic bag in the foldscope kit but you can experiment with the paper slides included also.

## 📲
## Phone Viewing

We have found that the [Phone Viewing Method](https://www.youtube.com/watch?v=0iRCceGCGus&feature=youtu.be) is the best way to to get images which isn't really made clear on the official guidance. You **can** hold it up to your eye and day light but really many of us love sharing our images with a phone so we'd like you to try get used to that.

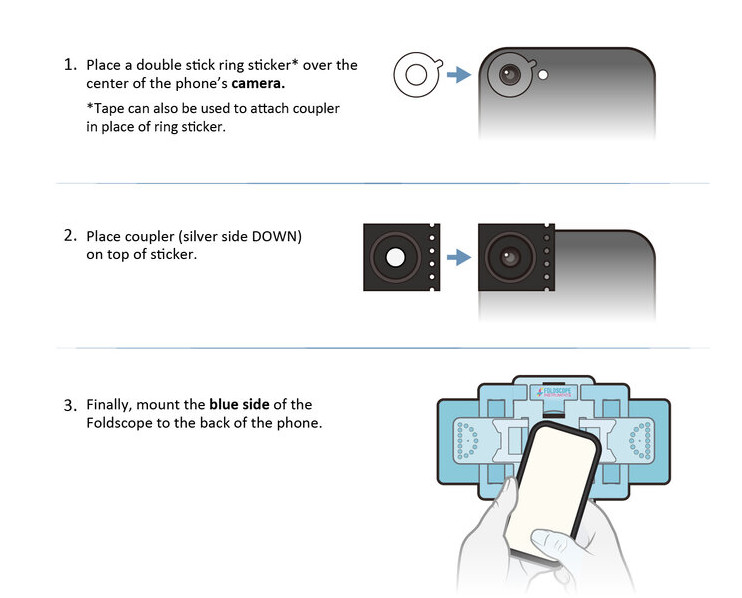
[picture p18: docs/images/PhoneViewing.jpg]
Foldscope phone viewing guide


There's a helpful [video tutorial](https://www.youtube.com/watch?v=hDIBLYLK_kg) that's well worth checking out.

We've also found resting on a desk and tilting the phone with the 'scope attached up to light reflected from your desk or laptop is enough illumination. We suggest phones to do most of our viewing.

It's worth noting aswell that the original [Foldscope Academic Paper](http://arxiv.org/abs/1403.1211) imagined the Foldscope could be a xenodiagnostic tool to identify host/parasites in blood and urine samples, or do haemocytometer counts, so viewing such samples at a safe distance with a phone is essential. The foldscope works with glass slides really well in addition to the paper slides included in the foldscope pop-out 'net' where you assembled all your foldscope components.

Practice capturing images before you make your first moulds though!

## Quickstart: Minimal Foldscope Assembly for Phone Use 🔬📲

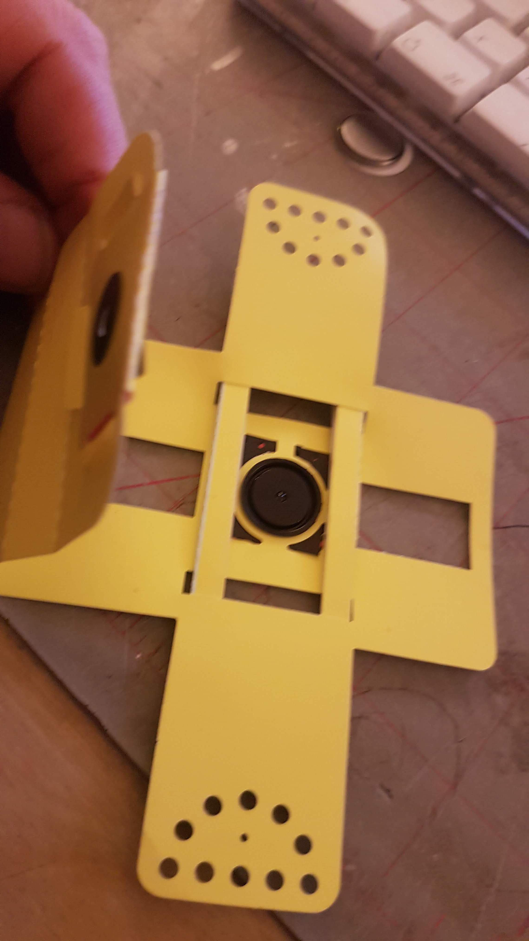
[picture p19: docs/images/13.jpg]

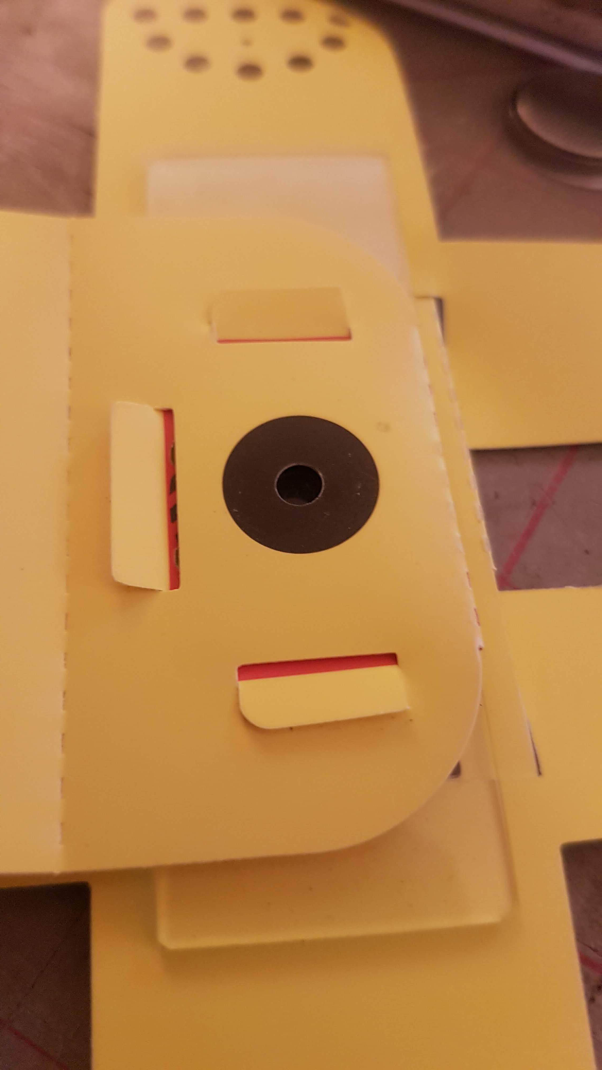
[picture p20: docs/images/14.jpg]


The full build as described in the video is best for general use and practice so get used to that first - it's quite easy to take away the stage later on. This method is useful if you want to swap between many different slides often with your phone.    

Open up your foldscope kit and open the instructions. We are going to just build up just the lens stage and focus ramp, a minimal build to look at some algae and make moulds and connect to our phone cameras. Basically you follow Steps **1** - **6** in the main Foldscope **ASSEMBLY INSTRUCTIONS**, ie the Instructions in the press out net that the 'scope sits inside, and step **10**. of the

This method ignores the blue sample stage that lets you hold and move around the sample on the slide, and just uses the magnetic assembly to hold the slide in place. Then turn over the 'scope and follow the instructions of phone use to capture images and lift the phone and magnetically attached 'scope to the light of a window or laptop screen.

## Back in Time ⌛

When microscopes were first used people did not know what they were looking at; what was a new organism or an artefact of the lens or a tiny lump of grease from a finger? Early geneticists, long before they imagined 'seeing' a gene, would often ban them from the laboratory as unreliable. We've come a long way.

In many ways the foldscope puts us back in time as we struggle (and it can be!) to see something. However you'll be surprised just how much you actually tacitly 'know' about what you are looking at. You'll intimately 'know' when you see the algae or a plant cell sample. Unlike laboratory 'scopes' your tiny hand movements and fiddling with your phone are very visible, you actually get to 'feel' when you are seeing something. This is a bit like Ian Hacking's idea of 'Intervening'; we 'see' with microscopes partly because of this awareness of how we are interacting with the sample.

>Remember, with microscopes we are mainly seeing light being **refracted** 'through' an organism when in our world we only ever really see light reflected off the surface of an object.

## Foldscope Ready 🔬

Once you have managed to successfully view the included sample glass slide in the foldscope and got to grips with the phone view, check out your Lab From A Chip booklet.

Again if you are taking part in the online workshops, don't start the moulding process, just familiarize yourself with the kit and process and play with the paper slides, we'll do the moulding together!

Below are additional notes to complement the instruction booklet included in your Foldscope kit bag.

Your kit should include, in addition to the foldscope, [this inventory of components](#inventory)

### PDMS Slide prep 💉💉

You should now be fairly confident you can image things with the Foldscope and take an image with your phone. The next step is making moulds with PDMS silicon. There are two component liquids that when mixed will start to cure into a clear solid. Follow all the instructions in the booklet provided. Below is the summary of what you need to do for quick reference if you dont have your booklet with you.

To safely store and transport the PDMS we've had to put them in pouches - each pouch has 4-6ml of PDMS component but it can be awkward to syringe. You only need a small amount to mix in - 0.4ml, but you may end up with air bubbles in the syringe. Hold the syringe vertically with the tip pointing upwards and wait for the bubbles to rise to the surface then gently push the liquid up to the tip - you want it to be as free of air bubbles as possible.

An alternative is to squeeze empty the pouch into another clean narrow container and then syringe up the contents - you can keep the syringe full for other experiments and store it in the packaging or if you are worried about leaks syringe back into the pouch - but dont get them mixed up!

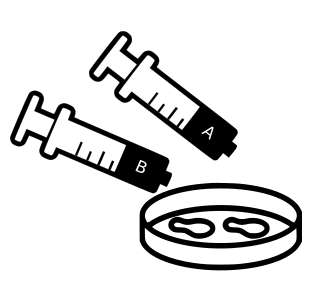
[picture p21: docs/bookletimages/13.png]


Inject equal amounts (no more than 0.4ml of each) of silicon from syringe A and fixer from syringe B into the 'floor' your mini petri dish (it's the smaller diameter part - the wider diameter part is the lid)

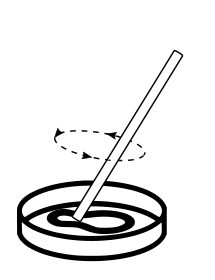
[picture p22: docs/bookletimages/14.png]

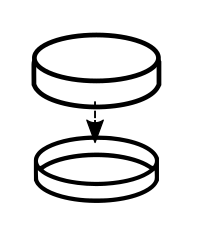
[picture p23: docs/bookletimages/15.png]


Mix well with a clean spoon or rod to remove bubbles and put the lid on.

## Making An Impression 📥⌛

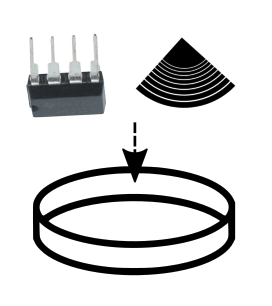
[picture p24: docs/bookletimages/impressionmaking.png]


You now need to make an impression in the PDMS mix after mixing. To do this take your black viny fragment and with tweezers gently submerge it grooves facing up in the bottom of the dish. You want there to be a thin film or slab of silicon over the top. Over time the liquid settles perfectly perpendicular so make sure there's enough to keep the vinyl submerged - but not too much - we are aiming for a thin slab of silicon with an impression in it. Then take the `555` timer chip and bend the metal legs at each corner upwards so that when placing the chip logo down into the PDMS in the dish you end up with a thin film of liquid between the chip surface and the bottom of the petri dish. Press it gently into the mix and you'll end up with a 'slab' of silicon under the chip with an impression of the logo and text of the chip surface - the metal legs keep it less than a mm above the surface of the bottom of the dish. This is tricky, press too hard and your section of PDMS is too thin to remove in one piece with the chip markings once it hardens. The vinyl record grooves face up submerged in the liquid there should be a thin film Usually just resting it in the mix is enough providing you dont drop or move the petri dish too much after.

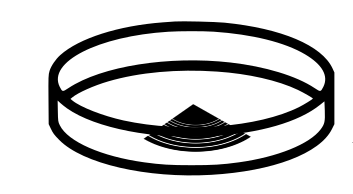
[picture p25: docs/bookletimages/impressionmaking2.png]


Now you need to wait and let it set! This can take, depending on thickness, up to 48 hours at room temperature but we've found just leaving overnight is fine

## Tips

### Temperature ⚠🔥 ️

In a warmer place or in sunlight it's alot quicker, some suggestions of heating to 70 degrees Centigrade estimate fully setting in 2 hours.

We `**DO NOT**` recommend heating to any temperature you can't touch safely, like a radiator but you should not leave it unattended. Anything over 70 degrees and your petri dish will melt. In our case also, using the vinyl fragment, it is safest to just leave it in warm room overnight or in direct sunlight. You really `**DO NOT want under ANY circumstances to overheat or burn your vinyl fragment**`. Vapourising or burning vinyl (150 degrees and up) can release chlorine fumes that even in tiny amounts inhaled can be extremely dangerous.

### Other Techniques

You can of course make more impressions in other containers with the `A` & `B` mix.

While you wait practice with your foldscope and experiment viewing your algae and other things without your PDMS slab. The paper slides and plastic clear coverslip stickers provided also are worth experimenting with.

### Bubbles

There is another step when making microfluidic moulds, making a vaccuum in a degassing chamber to remove any bubbles. For us this is too difficult; although there are plenty of nice DIY vacuum chamber designs out there, [This DIY chamber is our favourite](https://www.youtube.com/watch?v=k-64AgZp9OE) but we've found you can get ok results without this, the bubbles tend to leave naturally and don't reallly affect our results as we don't mind a few bubbles in our images, they might be intersting objects for the algae to swim around.

## Removing and Placing our PDMS slab🥢

After leaving your 'slab' of PDMS in the petridish overnight we need to carefully remove it. So we need to carefully remove the fragment from the mix. Now cut, preferably with a scalpel or very sharp fine knife, (sorry we can't include that) the 'slab' with our impressions in them and very carefully scrape it from the dish surface with a tiny flathead screwdriver then lift it with your included tweezers.

Now carefully place it impression down onto the glass slide. If it breaks (which it often does!), dont worry! get what you can onto the slide.

### Tip
Always be making extra slides for next time! The chips and vinyl can be re-used, just peel out the unused silicon. You may want to find other petri dishes or similar containers

## Placing Our Algae in Our PDMS Slide🐛

Get your disposable micro-pipette and capture a drop of algae, being careful not to spill the remaining algae culture.

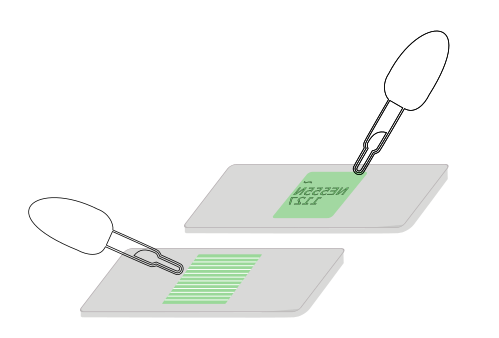
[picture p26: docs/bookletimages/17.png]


Use the micro disposable pipette to inject a drop of the algae suspension onto the slide and then with tweezers place your PDMS slab on top. You can also try letting capilliary action pull the liquid and our algal friends into the grooves into the gap between the tiny impressions of the chip surface markings or the vinyl channels and the microscope slide.

Now carefully add a cover slip sticker over the top to 'trap' the liquid and slab.

## Fixing to the foldscope.

You want the cover slip on the top of your slide or the slab to face the ball lens on the yellow underside of the 'scope. You can unfold the magnetic section and then when you can see your sample is over the lens, let it snap back and this is often enough to keep your sample in place when viewing

You can also use it without the full foldscope frame; a minimal setup for use with the phone view as below




### Fixing more securely

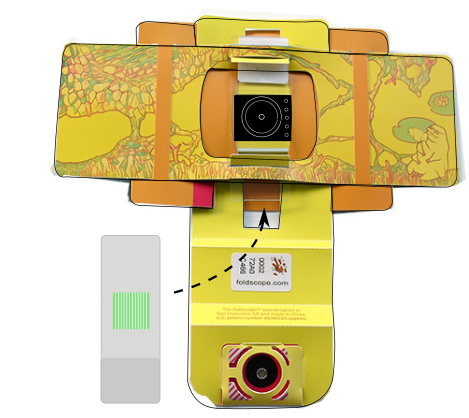
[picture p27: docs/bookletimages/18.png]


You can insert it more securely than in the minimal Foldscope build following in diagram above

Make sure you have got used to inserting and securing a glass slide into the Foldscope. When first doing it it's really difficult, the Foldscope coated paper is surprisingly resilient; you'll need to stretch the slots by inserting and removing a clean slide in and out of the slots of the paper platform so you can move it around easily to find and focus your slide and PDMS slab. It takes practice and some skill.

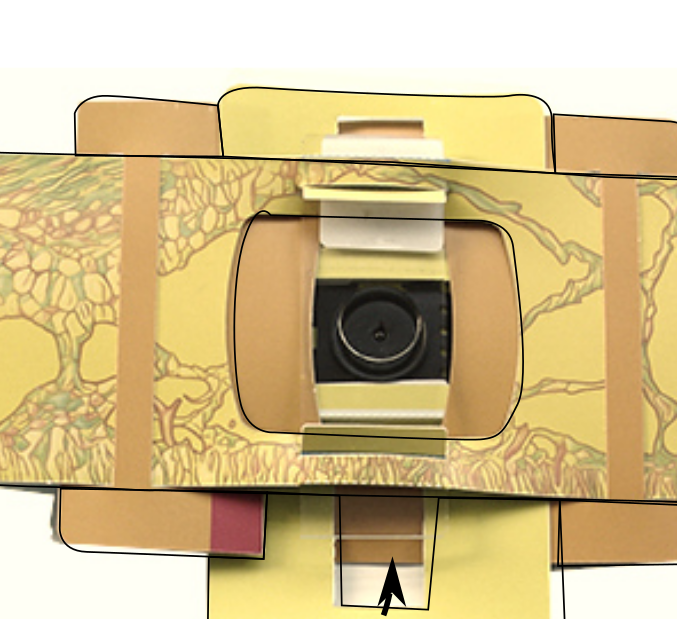
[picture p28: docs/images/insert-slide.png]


Insert your slide into the Foldscope as below (be careful slotting it in not to push your PDMS slab or coverslip away)

### Cover slip Tip

 We found using the re-useable glass slide and the included clear plastic sticker coverslips work really well even with thicker slabs. They are in the Foldscope plastic bag and you can peel them off; bend the backing sheet so you can lift off a corner of the clear coverslip stickers, then use tweezers to place over your slab and algae suspension and seal them in.

You can still lift up the sticker and add water if the suspension starts to dry up

### Algae death

You will find that the longer you use the slide our Eugelena will start to move slowly as the water suspension dries up, eventually killing our collaborators. There is not too much to do about this and for us it brings up close, the issue in much experimental biology and indeed biotic gaming, what are the ethics of observing, using, and killing model organisms? For uni-cellular life like algae with no complex nervous system it's a difficulty one can learn to accept, but we should think about what does it take for one organism to use another as a model, and for which organisms would this be unacceptable.

You can keep them alive longer by adding water or drop used slabs and coverslip stickers in a jar of water and left in sunlight occasionally allowing gas to exchnage they will happily multiply asexually and eventually form green algal blooms if you're lucky!

Waste and death of organisms takes place on a vast scale in microbiology, made worse by contemporary practices of often essential asceptic technique that use throw away plastic tips and tubes and petri dishes (which we use in our kit). Years ago re-useable glass was so much part of microbiological practice that every biology department had an in-house glass blower and it meant disinfecting and cleaning equipment was as important as inoculation. Crucially this is a part of the culture of re-use and care so important to the life sciences, that we could be losing.

## Get Exploring

That's it! You're ready! Now setup your phone with the Foldscope [as above](#phone-viewing) and see if our algal friends have found their way into the microfluidic channels. We've found that the vinyl record is the most rewarding, as you really get to see our *Euglena gracilis* moving along the grooves and you could try imagine how slow the music might sound like at their speed. With your phone setup you could try shining the LED included and see how they respond.

These organisms are mixotrophic in that they 'eat' proteins and plant matter but also photosynthesise, so like plants 'make' food from sunlight. They are like plants but also behave like animals.

Have a think what other ordinary stuff we have in our homes and workplaces that might have tiny spaces the size of record grooves or silicon chip logos? What about textiles? The surface of your phone or pair of running shoes/trainers/sneakers? An old pair of headphones? The surface of some wood or steel? Once you put yourself in the Algae's position the human engineered world becomes like a whole world.

You begin to realise the most ordinary stuff in our human engineered world is full of vast precision engineered space and constructions, weird artefacts of utility that at some point took alot of human care and often untold human and non-human cost

### Share Your Experience

Please post your images to twitter and copy @CriticalKits and @PrakashLab or Instagram @cheapjack @foldscope

### Taking part further

Finally if you'd like to take part in the CriticalKits research project please contact <a href = "mailto:r.dalziel@lancaster.ac.uk?subject = Lab From A Chip Kit&body = My PIS sheet and consent">Ross Dalziel</a>

### Other Materials

You might like to try using other materials. One tip for making moulds on big surfaces that dont fit a little petri dish is to use rolled up plasticine to make tiny 'walls' for your mould, if you try paint the PDMS on, it just spreads too thinly otherwise!

Ideally you want little PDMS 'slabs' of 0.25mm thickness or less.

### Inventory

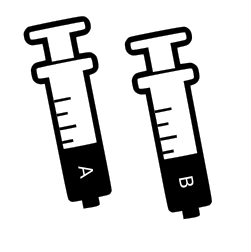
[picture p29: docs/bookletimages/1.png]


Prepared & labelled syringes filled with PDMS (A) & hardener (B). PDMS is a non-volatile silicon and safe to handle, but not ingest. We advise taking care to wash your hands thoroughly after use and store them in the already open plastic sleeves. Unmixed they store for up to a year. Be careful not to cross contaminate the A & B components or they will harden in storage.

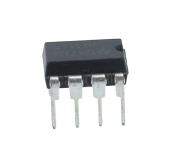
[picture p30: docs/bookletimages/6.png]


555 Timer chip. Common chip in maker projects. See https://github.com/DoESLiverpool/WearableTechBadgeWorkshop/blob/master/555Tutorials.md for what you can make with timers.

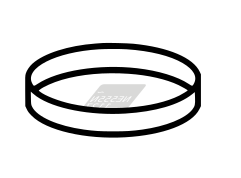
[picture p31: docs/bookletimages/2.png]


Micro-petri-dish with lid. Mix PDMS together and make impressions with chip surfaces. You could use anything you think might make tiny  impressions in the surface of your PDMS mould.

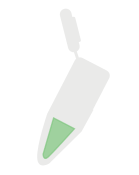
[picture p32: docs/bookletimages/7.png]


1.5ml Eppendorf with safe-lid containing an algae suspension of Euglena gracilis. You can see Euglena [in action here](https://youtu.be/ghMFiTQJU-M)  

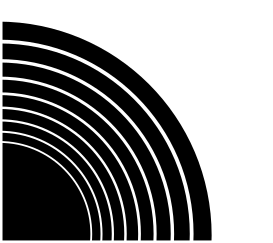
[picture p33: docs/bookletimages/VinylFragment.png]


Vinyl fragment. Some of you may not remember, but at the dawn of pop culture and capitalism music was distributed widely on vinyl discs as micrometre scale grooves that could be amplified and played back



1.3ml Disposable micro pipette

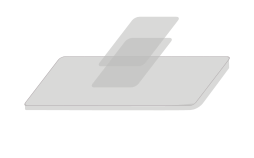
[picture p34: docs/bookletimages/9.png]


Blank glass Microscope slide for use with the cover slip stickers

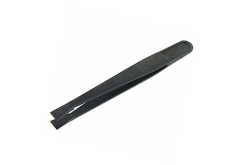
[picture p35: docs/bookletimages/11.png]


Plastic tweezers for removing your set PDMS impressions

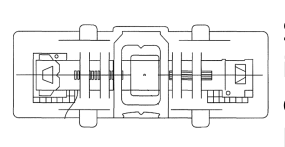
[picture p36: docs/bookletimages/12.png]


Standard Foldscope classroom kit, instructions, sticker set, lens cleaning q-tip, lighting stage and lens/phone assembly

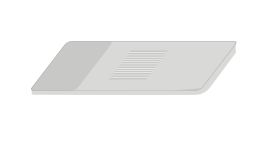
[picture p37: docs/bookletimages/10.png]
Picture of prepared slide


Pre-prepared stained slide for reference and testing.



Vinyl record Fragment. Some of you may not have a record collection and listen on big data infrastuctures like Spotify or YouTube or maybe if you care about artists getting paid, Bandcamp. You can't really get impressions from these sources although if you could access their server racks in the correct data centre you could find a hard drive that likely has some micro-engineered structures but you'd get in trouble!

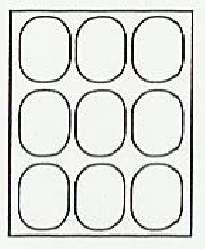
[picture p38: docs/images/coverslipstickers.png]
Picture of coverslip stickers


Cover slip stickers

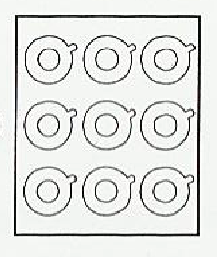
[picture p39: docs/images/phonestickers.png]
Picture of phone stickers


Ring stickers for fixing the 'scope to your phone camera

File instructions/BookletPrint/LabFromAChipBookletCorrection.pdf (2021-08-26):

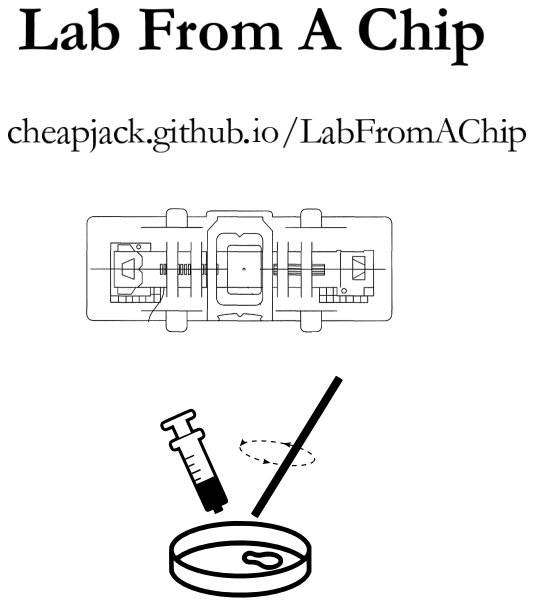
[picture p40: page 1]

Lab From A Chip is a DIY intervention in lab-on-a-chip technology inspired by science & technology studies (STS) and the history of microbiological technique. It's part of Ross Dalziel's Critical Kits project, at the Division for BioMedical Life Sciences at Lancaster University (BLS) and makerspace DoESLiverpool making add-ons for the Foldscope, a folding paper microscope by Prakash Labs.

"A lab-on-a-chip is a device that integrates one or several laboratory functions on a single integrated circuit of only millimeters to a few square centimeters" Wikipedia

We've packaged up the existing, friendly & cheap Foldscope kit, alongside some materials to follow the innovative practice of scientist & engineer Alexandre Benedetto & colleagues at BLS. They make cheap robust PDMS microfluidic environments to observe model organisms using old vinyl audio records as moulds - it's a DIY shortcut to microfluidic engineering on the cheap that feels like a makerspace strategy. We've tried to make it accessible to microscope newcomers & old-timers so you can watch Euglena gracilis, a light sensitive, highly motile algae swim amongst some of the amazing hidden structures that make up the everyday surfaces of the human engineered world. It's a way of getting materially engaged with other worlds & scales and perhaps develop feelings for other (micro) organisms.

# Lab From A Chip:

The first step is to assemble & practice the use of your Foldscope. All the components and instructions are included in the bag and can be popped out & folded out of the cardboard net - we've also included a glass reference slide to practice. Give yourselves some time to experiment with this before attempting moulding!

Then experiment making your own simple micro-moulds from the PDMS silicon, fragments of vinyl records & surplus electronics included. The Foldscope is a deceptively simple ball lens microscope, like the very first microscopes of Antonie van Leeuwenhoek, but made with the technology of advanced capitalism. You'll need to get quite intimate with your equipment to be able to 'see' with it - in many ways you have to 'feel' your way - to capture the images on your phone
- you see & feel exactly how your every movement intervenes in the microbiological world. Historian Ian Hacking thinks this is how we 'see' with microscopes - that intervening is crucial to the everyday 'doing' of science and also thinking about it's consequences.

This is a rough guide - experiment! - the first scientists did everything at home, years before having specialist objects like syringes. What other domestic materials can you find that might make tiny spaces we can use? Tell us about it!
Tweet @CriticalKits or the foldscope team at linktr.ee/ foldscope - look for help on the website on the cover.

## Getting Started

A

Pouches of PDMS A & B with labelled syringes. PDMS is non-volatile silicon, safe to handle, but not edible. We advise washing hands after use & storing syringes in the plastic sleeves. Unmixed it can store for years. PDMS has amazing 'resolution', getting into the smallest nook & crannies of our worlds...

## Inventory

555 Timer chip. Common integrated circuit - a silicon chip in digital maker projects and many electronic devices.

Petri-dish with lid. Mix PDMS & make impressions with chip surfaces. You can also use plasticine or bluetack to form even smaller moulds. It can take 6-10 hours at room temperatures to set but alot quicker in a warm dry environment. You can heat it but be careful not to melt the petridish and never do so and leave unattended!

Vinyl fragment. Some of you may not remember, but at the dawn of pop culture music was distributed widely on vinyl discs with micrometre grooves that could vibrate a needle so you could listen to music like Little Richard or Lover's Rock

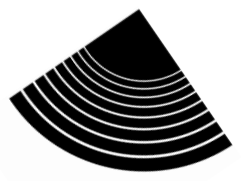
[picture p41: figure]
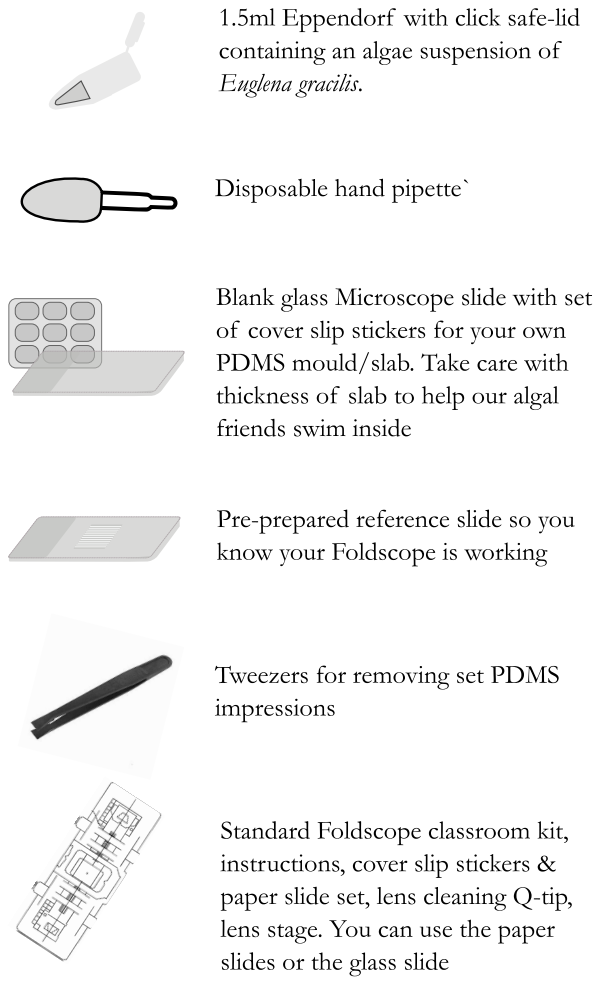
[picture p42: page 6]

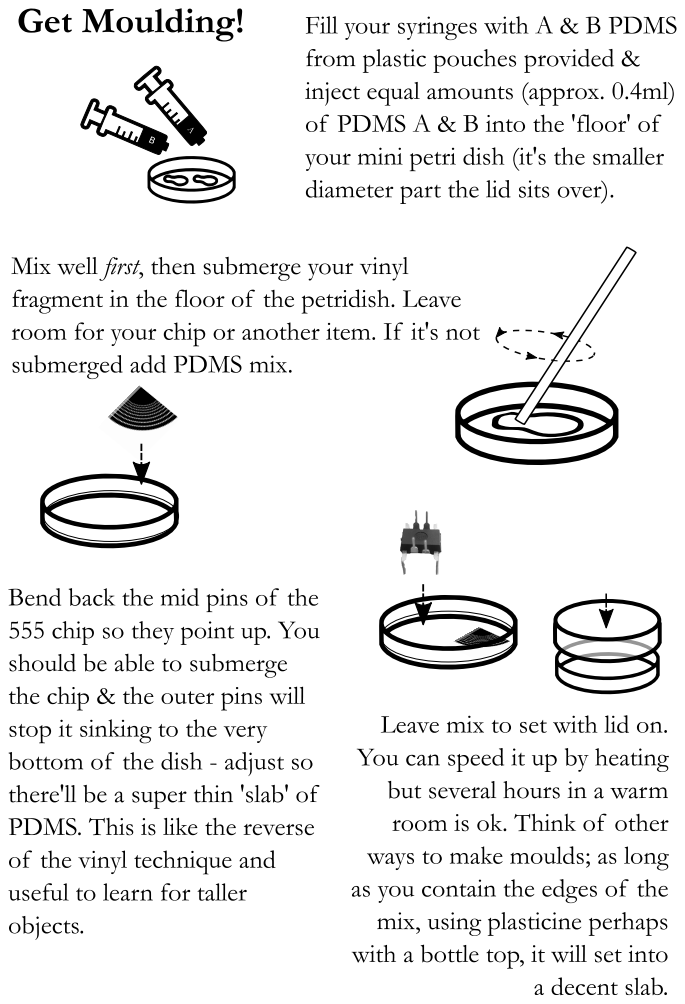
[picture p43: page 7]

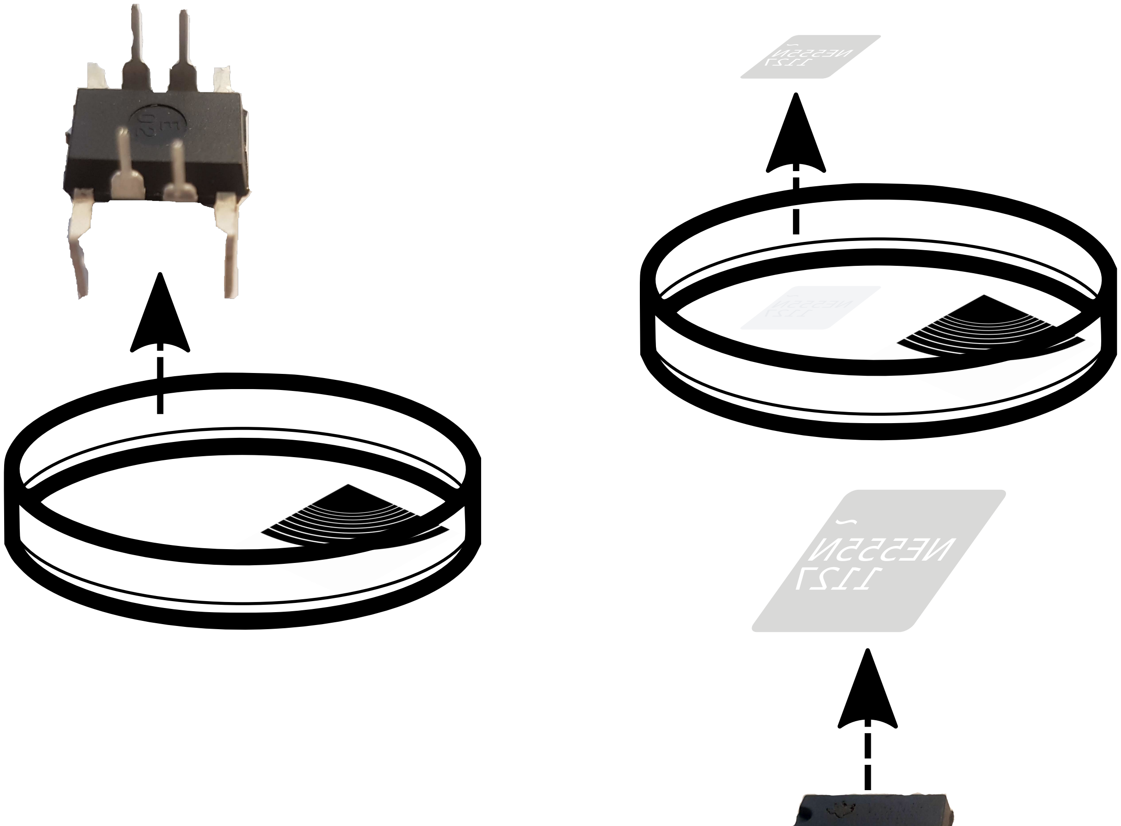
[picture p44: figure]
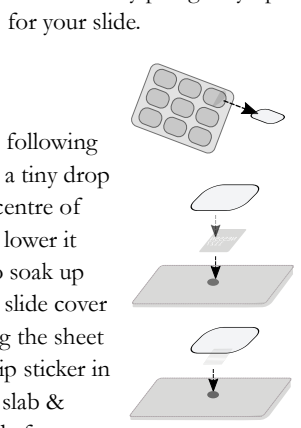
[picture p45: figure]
for your slide.

Prepare a glass slide (or paper following foldscope instructions) - Pipette a tiny drop of algal suspension onto the centre of the slide, pick up the slab and lower it onto the sample. Use tissue to soak up excess suspension. Peel off a slide cover sticker with tweezers - bending the sheet helps. Now lower the cover slip sticker in one movement to 'seal' in the slab & liquid sample on the slide ready for viewing.

Use a sharp blade (not included) to cut a section out of the now solid set PDMS slab over the vinyl surface. Use tweezers to lift this 'slab' of PDMS and carefully place left of centre of your microscope slide 'groove' side down - you'll move it again shortly. As you lift it you'll see the ridges of the grooves shimmer in the light.

For the chip - cut around it, remove and it should pull a slab from the dish or leave impression. Then cut around the slab & try pull gently up

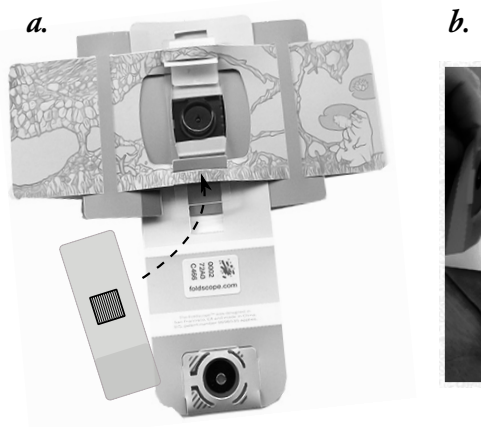
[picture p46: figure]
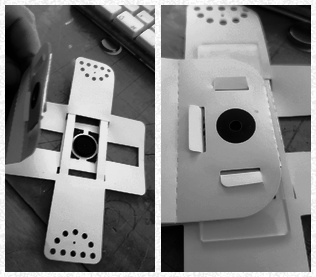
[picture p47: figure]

* Look for the key features of chip text so you know what to look for in the image - they can be hard to find and less deep than our vinyl grooves.
* An open laptop screen with daylight helps illuminate while phone viewing. Move the phone and 'scope around to play with the light as it is refracted through the sample.
* If your silicon 'slab' is too thick the foldscope might not be able to focus. Don't forget to adjust the folded focus ramp for focus issues (see Foldscope Instructions)

The example glass slide should've stretched the slide-holding slots so you can insert your new slide easily (a.). Be careful not to push your slab & algae off! It needs placing so the coverslip sticker top is closest to the lens - viewing on the blue side. For fast phone use you can remove the slide holding assembly (b.) and let the magnetic flap hold the slide.

## Tips & tricks

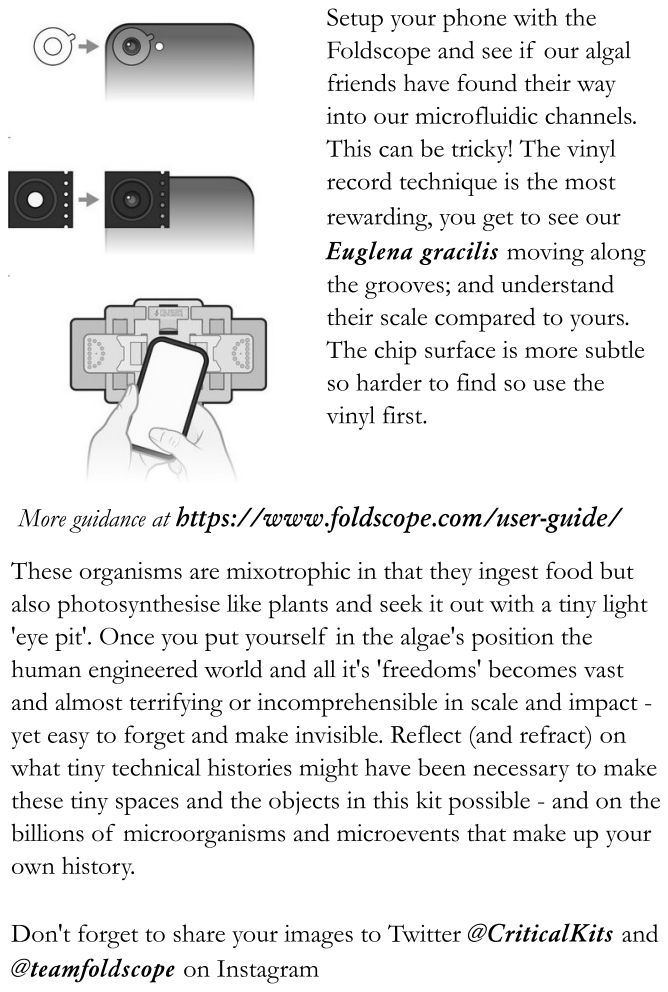
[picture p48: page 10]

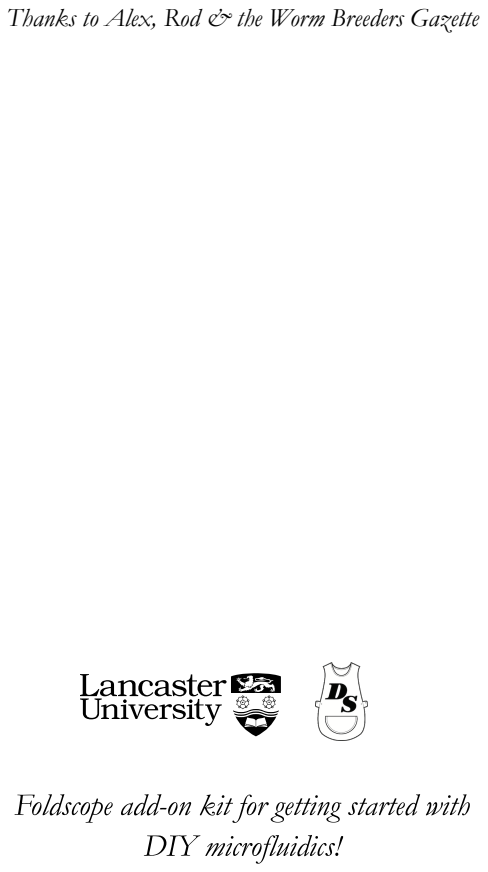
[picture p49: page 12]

Thanks to Alex, Rod & the Worm Breeders Gazette

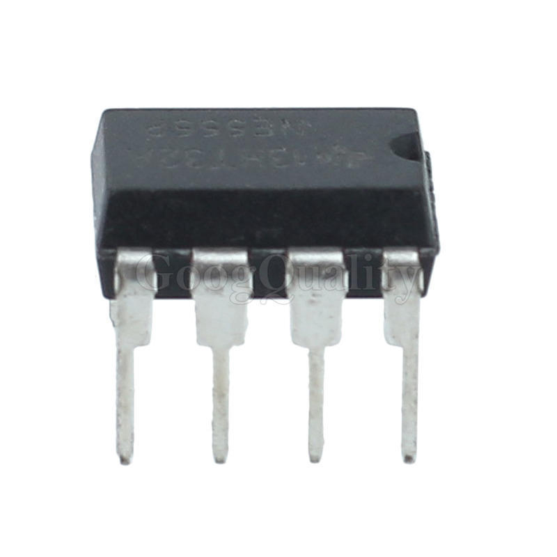
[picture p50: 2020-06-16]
instructions/555chip.jpg

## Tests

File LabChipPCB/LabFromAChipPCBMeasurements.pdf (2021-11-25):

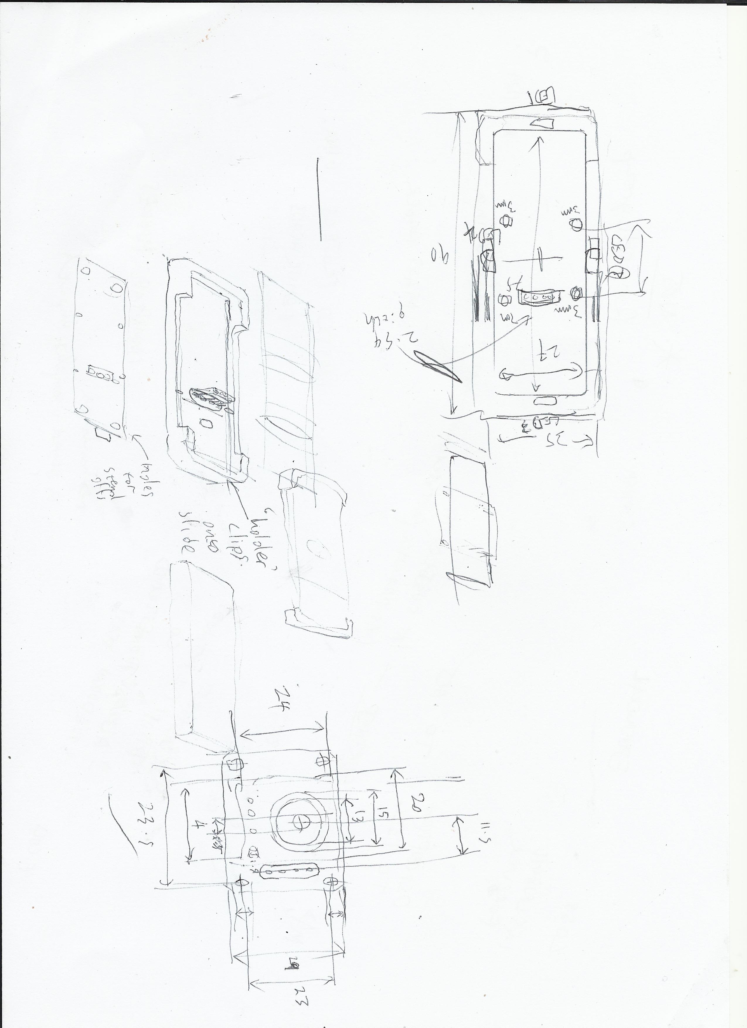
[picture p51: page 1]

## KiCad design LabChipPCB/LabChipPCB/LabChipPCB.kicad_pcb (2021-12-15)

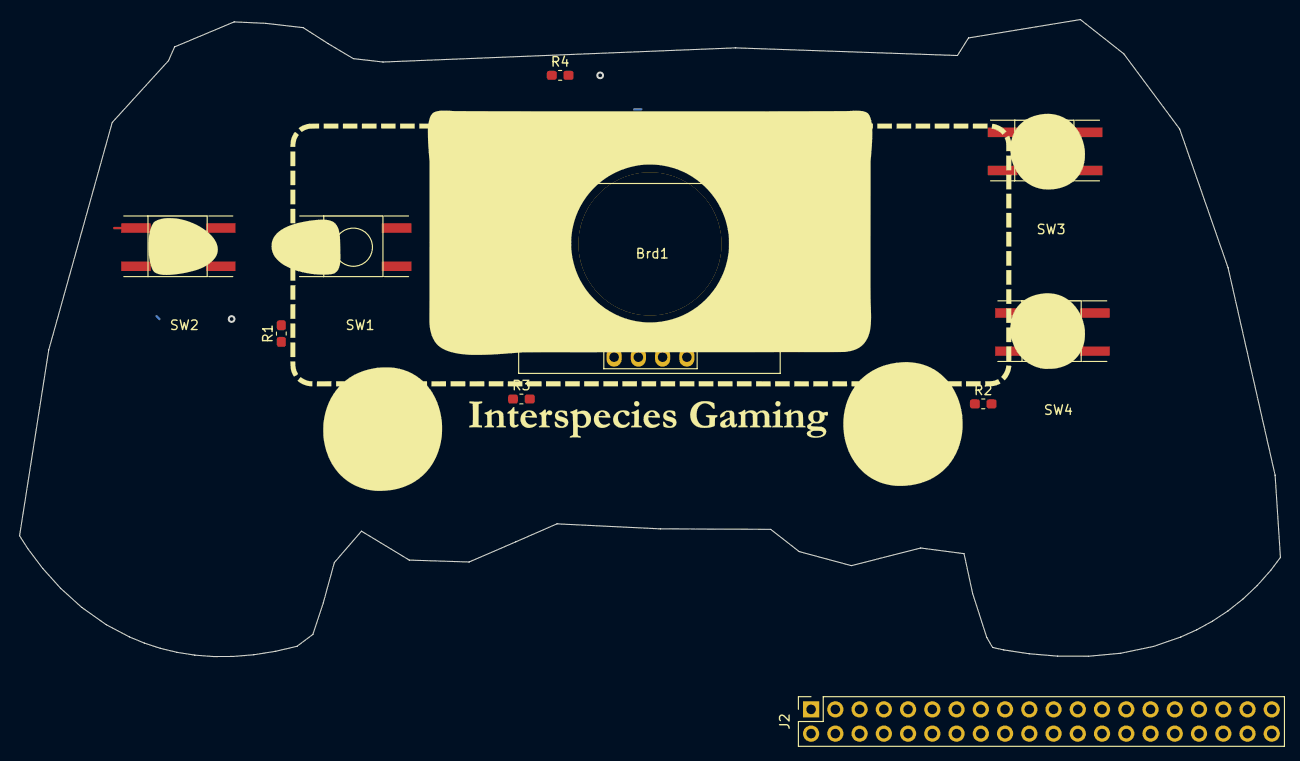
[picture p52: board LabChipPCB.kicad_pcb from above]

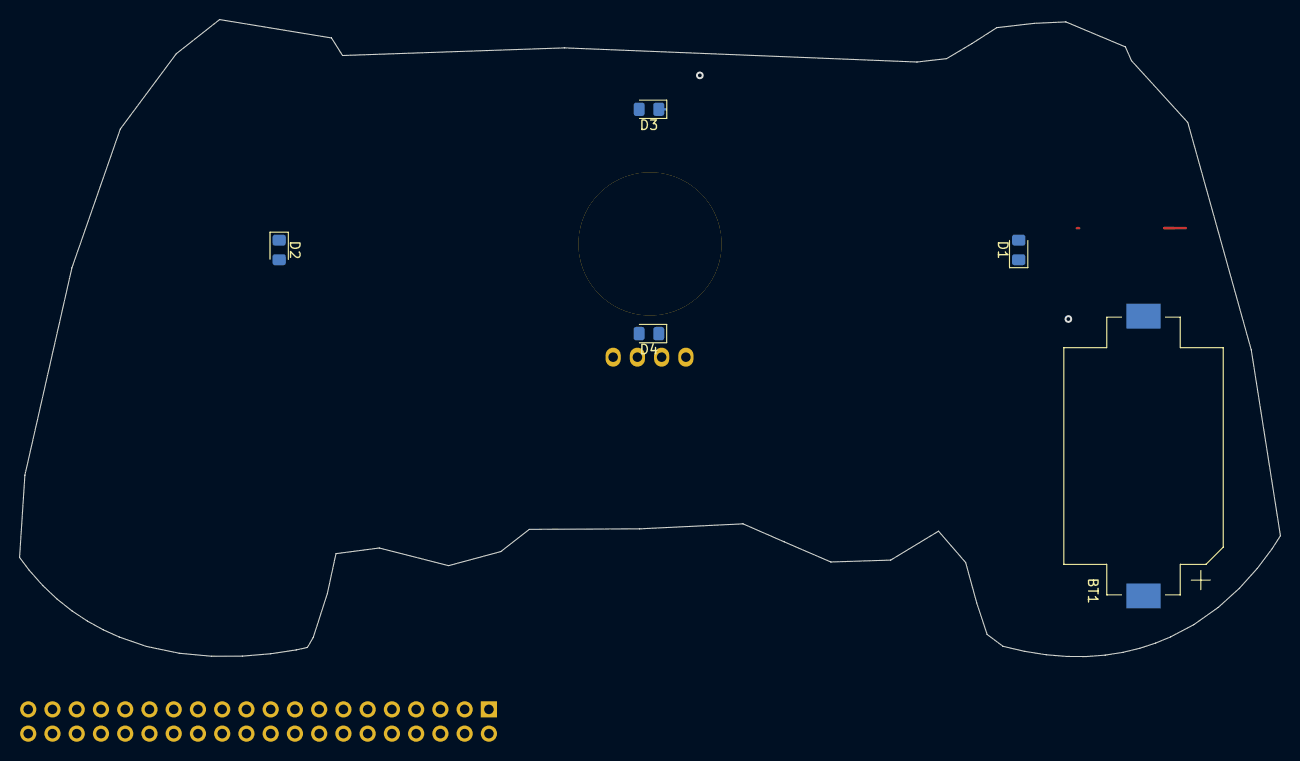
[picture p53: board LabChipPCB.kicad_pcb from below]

Board: 2 copper layers, 132.1 x 66.7 mm, 16 parts (5 on the bottom side), 12 nets.

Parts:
BT1: CR2032; BatteryHolder_Keystone_1060_1x2032
Brd1: SSD1306; 128x64OLED
D1, D2, D3, D4: LED; LED_0805_2012Metric_Pad1.15x1.40mm_HandSolder
J2: Raspberry_Pi_2_3_0; PinSocket_2x20_P2.54mm_Vertical
R1, R2, R3, R4: 220; R_0603_1608Metric_Pad1.05x0.95mm_HandSolder
Ref**: Val**; PSLayers1
SW1, SW2, SW3, SW4: SW_Push; Tactile_Pushbutton_LowProfile

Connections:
+3V3: BT1.1, Brd1.2, J2.1, SW1.1, SW2.1, SW3.2, SW4.1
GND: BT1.2, Brd1.1, J2.6, R1.1, R2.1, R3.1, R4.1
unnamed: D1.1, R1.2
unnamed: D1.2, SW2.2
unnamed: D2.1, R2.2
unnamed: D2.2, SW1.2
unnamed: D3.1, R4.2
unnamed: D3.2, SW3.1
unnamed: D4.1, R3.2
unnamed: D4.2, SW4.2
SCL: Brd1.3, J2.5
SDA: Brd1.4, J2.3

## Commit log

2020-03-04 added foldscope add on cardboard inserts
    [FoldscopeAddOns.dxf]
2020-06-14 Added artwork for the syringe net without the Pi Zero
    [FoldscopeAddOnPiZero.dxf]
2020-06-15 dxf for @JackiePease to kindly cut
    [FoldscopeAddOn1.dxf]
2020-06-16 fixed weird shrinkin g of svgs
    [FoldscopeAddOn1.dxf]
2020-06-25 missing LED image and booklet artwork
2020-06-30 detail on inserting glass microscope
2020-07-27 Alternative mould instructions
2020-07-29 updated instructions and removing pre-prepared PDMS ref, paperfuge and using alternative submerge moulding method
2020-08-14 extra materials tip
2021-09-10 removed the LED throwie as we've not included it in the latest kits
2021-09-13 clarify waiting til session to mould
2021-11-25 Added the KiCad files and updated Printed booklet for re-print
    [LabChipPCB.kicad_pcb, LabChipPCB.sch, PCBShapeWithSlide.dxf]
2021-12-15 pcb updates
    [LabChipPCB.kicad_pcb]
2021-12-17 Switch off power from the battery when there's power available from the Pi
    [LabChipPCB.sch]
2023-01-05 images and text for the PCB
